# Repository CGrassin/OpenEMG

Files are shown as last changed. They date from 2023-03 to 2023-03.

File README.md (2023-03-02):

# OpenEMG

Electromyography (EMG) is a commonly used electrodiagnostic medicine technique for evaluating and recording the electrical activity produced by skeletal muscles. OpenEMG is a project that aims to create an open-source, easy-to-make EMG module that can capture muscle information from Arduino or any other micro-controller. With this module, users can measure muscle activity and use the data to explore various applications such as robotics and prosthetics.

View the article about this project (including performance, usage, principle of operation) here: https://charleslabs.fr/en/project-OpenEMG+Arduino+Sensor

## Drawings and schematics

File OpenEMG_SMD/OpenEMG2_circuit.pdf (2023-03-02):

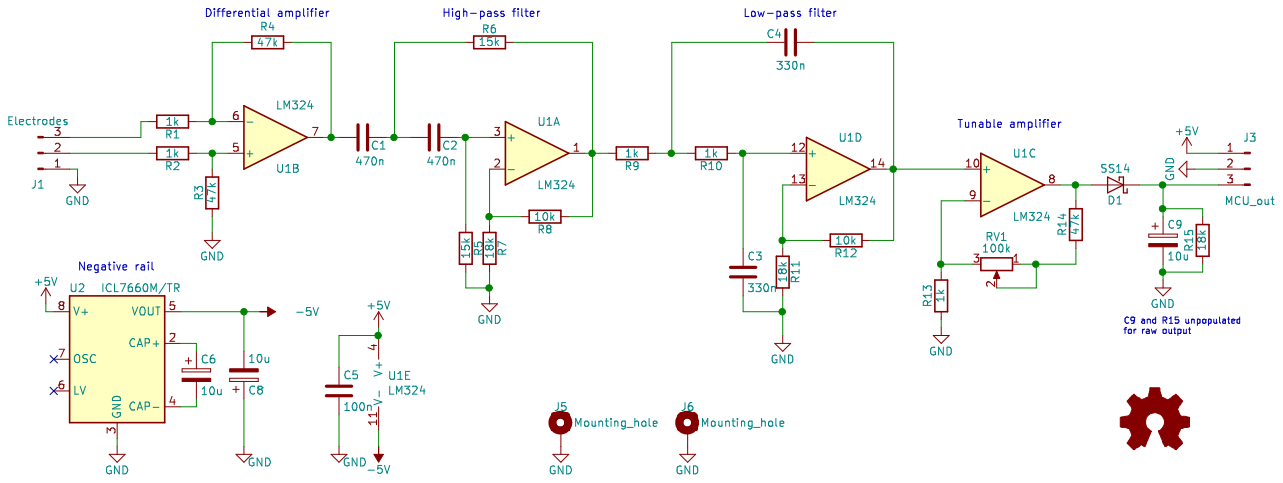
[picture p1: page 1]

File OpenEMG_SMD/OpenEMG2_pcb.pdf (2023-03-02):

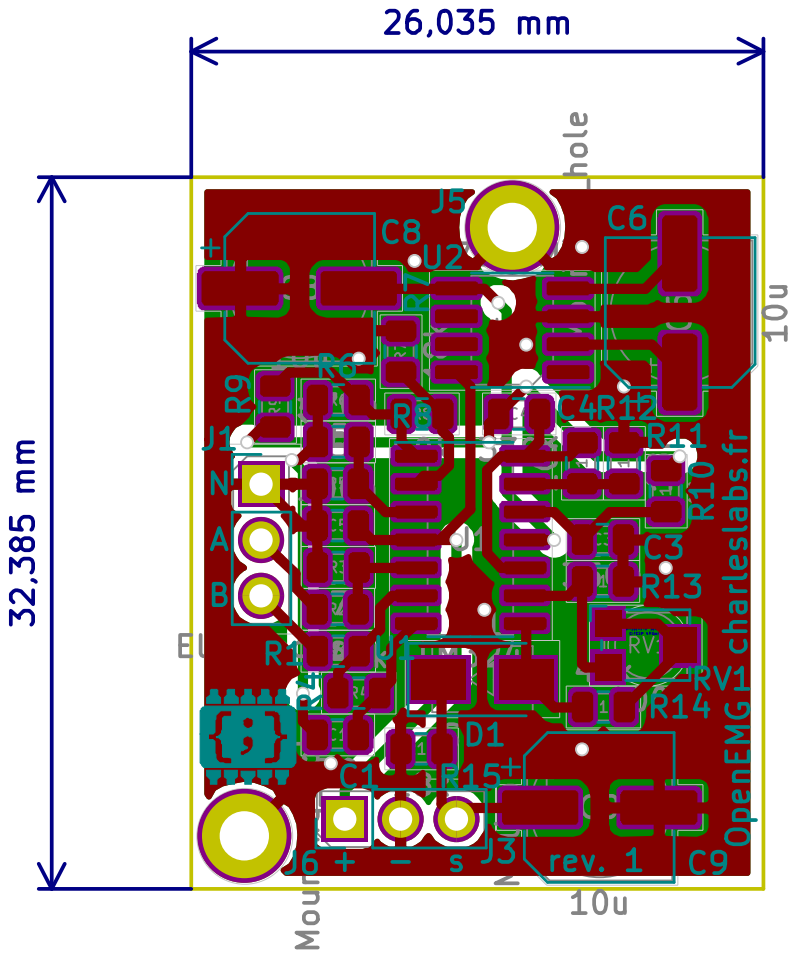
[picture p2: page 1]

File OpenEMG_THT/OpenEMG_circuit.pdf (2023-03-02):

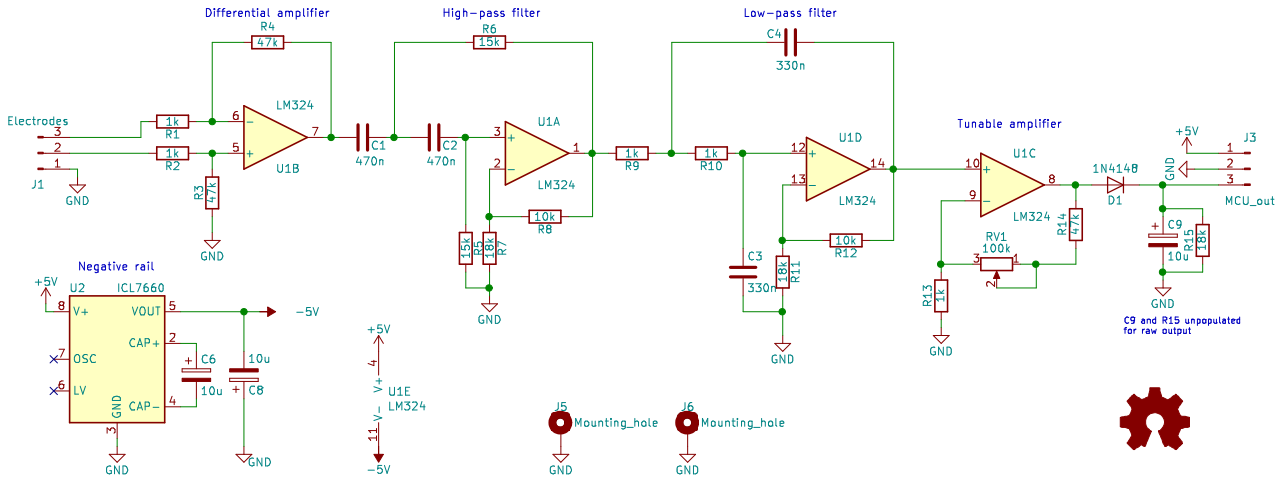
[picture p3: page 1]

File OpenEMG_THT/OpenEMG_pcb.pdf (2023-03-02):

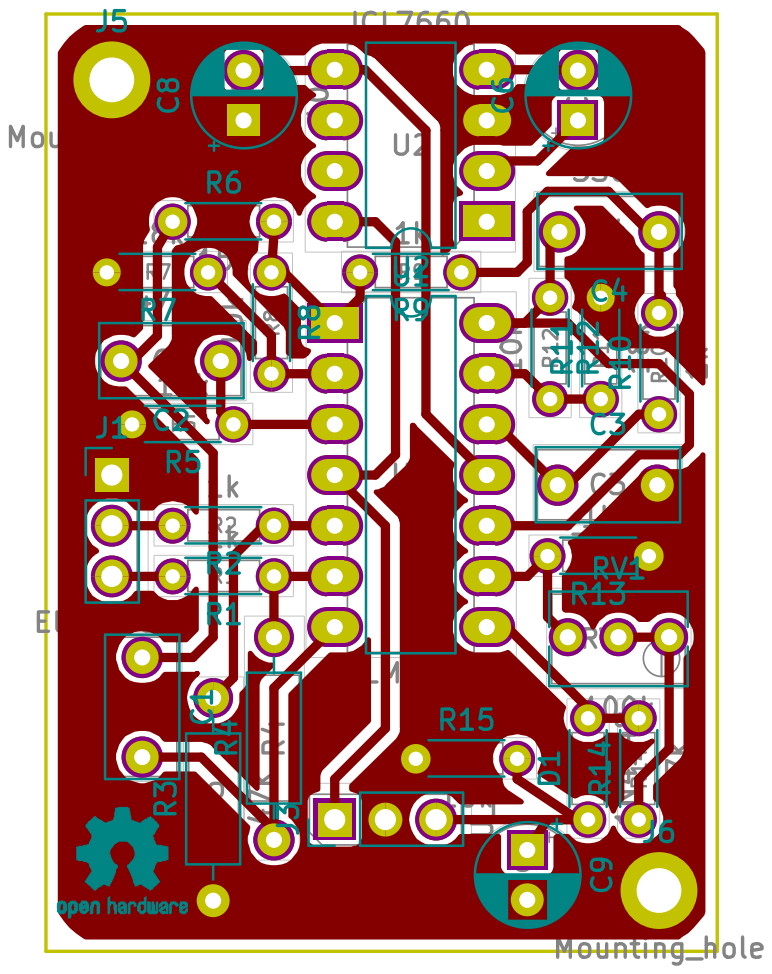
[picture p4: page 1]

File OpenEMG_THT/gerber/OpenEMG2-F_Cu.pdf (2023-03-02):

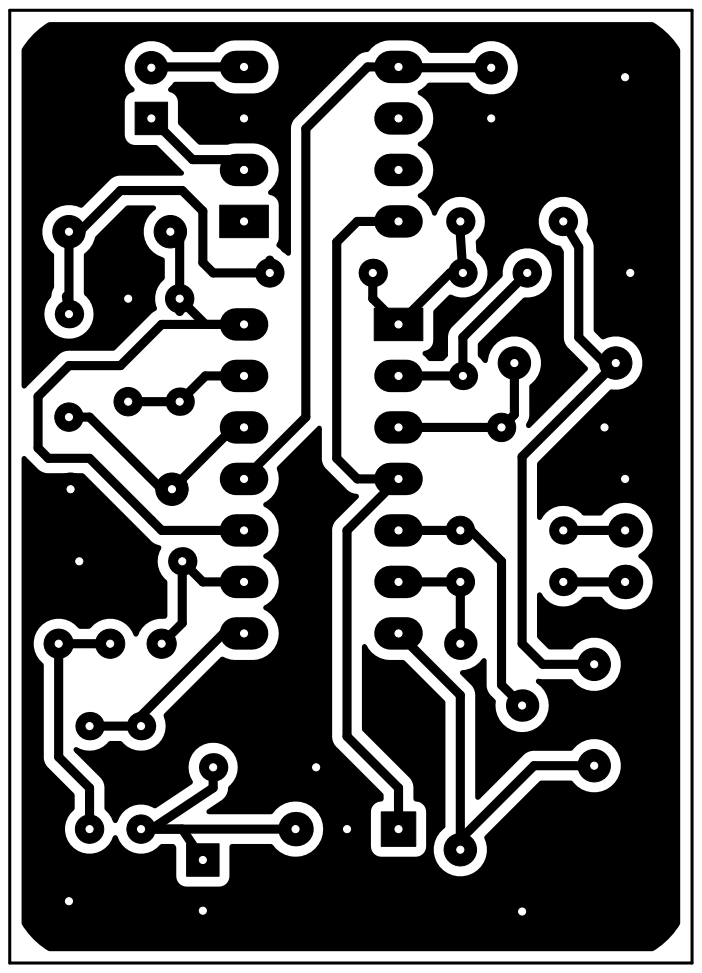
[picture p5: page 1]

File: OpenEMG2.kicad_pcb Sheet: charleslabs.fr Open Hardware

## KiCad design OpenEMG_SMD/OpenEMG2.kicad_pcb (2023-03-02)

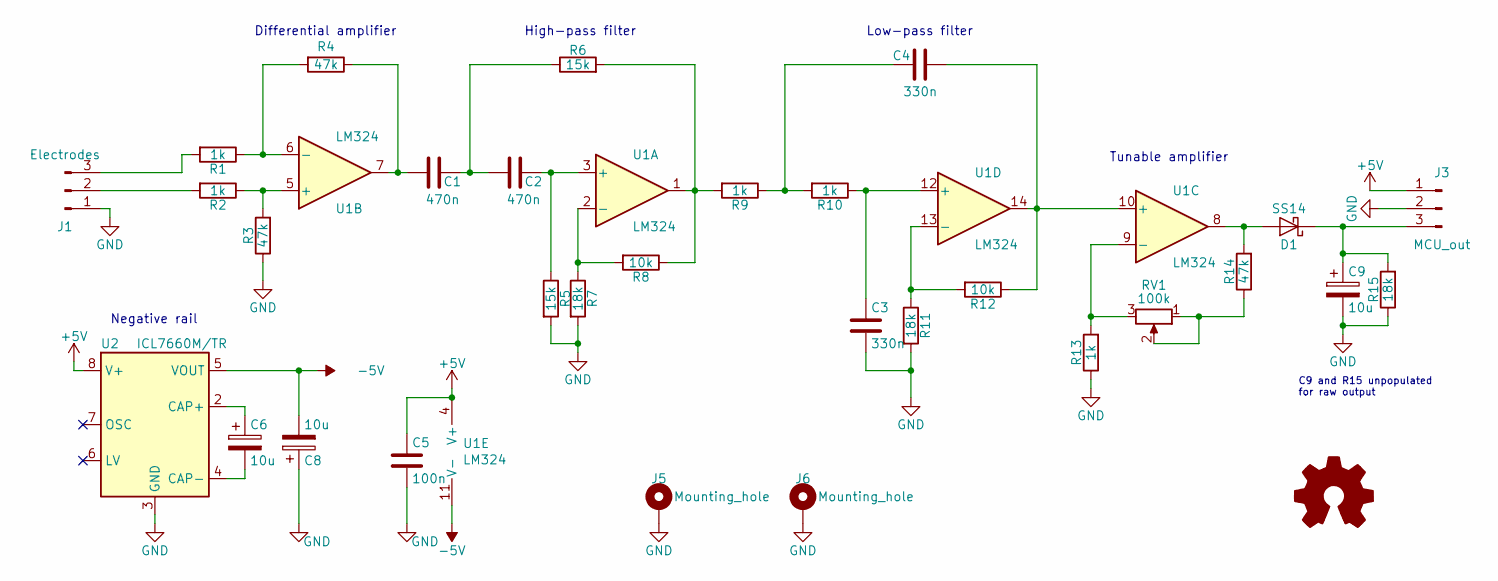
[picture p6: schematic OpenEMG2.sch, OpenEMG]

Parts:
C1, C2: 470n; C_0805_2012Metric
C3, C4: 330n; C_0805_2012Metric
C5: 100n; C_0805_2012Metric
C6, C8, C9: 10u; CP_Elec_6.3x4.5
D1: SS14; D_SMA
J1: Electrodes; PinHeader_1x03_P2.54mm_Vertical
J3: MCU_out; PinHeader_1x03_P2.54mm_Vertical
J5, J6: Mounting_hole; MountingHole_2.2mm_M2_DIN965_Pad
LOGO1: logo
R1, R2, R9, R10, R13: 1k; R_0805_2012Metric
R3, R4, R14: 47k; R_0805_2012Metric
R5, R6: 15k; R_0805_2012Metric
R7, R11, R15: 18k; R_0805_2012Metric
R8, R12: 10k; R_0805_2012Metric
RV1: 100k; Potentiometer_Bourns_TC33X_Vertical
U1: LM324; SOIC-14_3.9x8.7mm_P1.27mm
U2: ICL7660M/TR; SOP-8_3.76x4.96mm_P1.27mm

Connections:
+5V: C5.1, J3.1, U1.4 (V+), U2.8 (V+)
-5V: C8.2, U1.11 (V-), U2.5 (VOUT)
GND: C3.2, C5.2, C8.1, C9.2, J1.1, J3.2, J5.1, J6.1, R3.1, R5.2, R7.2, R11.2, R13.1, R15.1, U2.3 (GND)
unnamed: C1.1, C2.2, R6.1
unnamed: C1.2, R4.1, U1.7
unnamed: C2.1, R5.1, U1.3 (+)
unnamed: C3.1, R10.1, U1.12 (+)
unnamed: C4.1, R9.1, R10.2
unnamed: C4.2, R12.1, U1.10 (+), U1.14
unnamed: C6.1, U2.2 (CAP+)
unnamed: C6.2, U2.4 (CAP-)
unnamed: C9.1, D1.1 (K), J3.3, R15.2
unnamed: D1.2 (A), R14.2, U1.8
unnamed: J1.2, R2.2
unnamed: J1.3, R1.2
unnamed: R1.1, R4.2, U1.6 (-)
unnamed: R2.1, R3.2, U1.5 (+)
unnamed: R6.2, R8.1, R9.2, U1.1
unnamed: R7.1, R8.2, U1.2 (-)
unnamed: R11.1, R12.2, U1.13 (-)
unnamed: R13.2, RV1.3, U1.9 (-)
unnamed: R14.1, RV1.1, RV1.2

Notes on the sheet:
Differential amplifier
Tunable amplifier
High-pass filter
Low-pass filter
Negative rail
C9 and R15 unpopulated for raw output

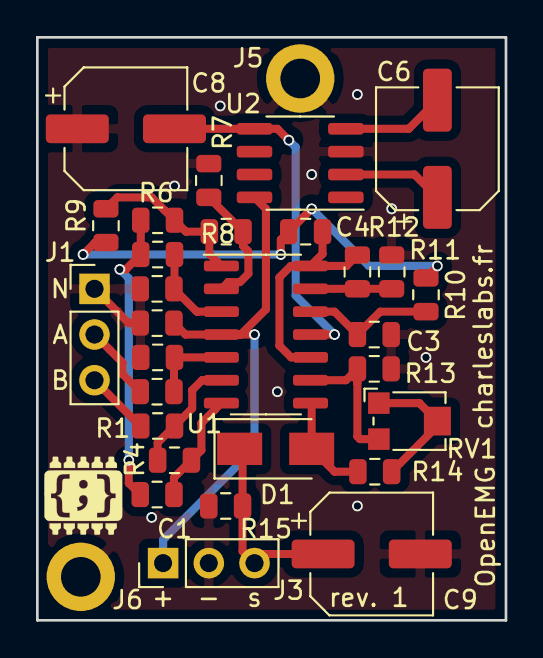
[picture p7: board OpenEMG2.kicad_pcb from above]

Board: 2 copper layers, 26.0 x 32.4 mm, 32 parts (0 on the bottom side), 22 nets.
